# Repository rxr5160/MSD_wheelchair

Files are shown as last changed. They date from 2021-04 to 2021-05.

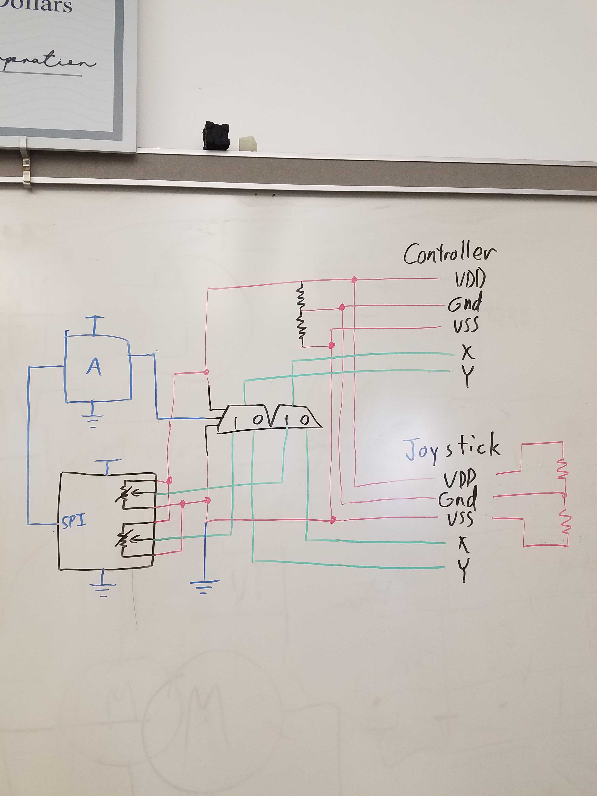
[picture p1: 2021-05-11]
Documentation/Media/Joystick/NewJoystickPCBdesign.jpg

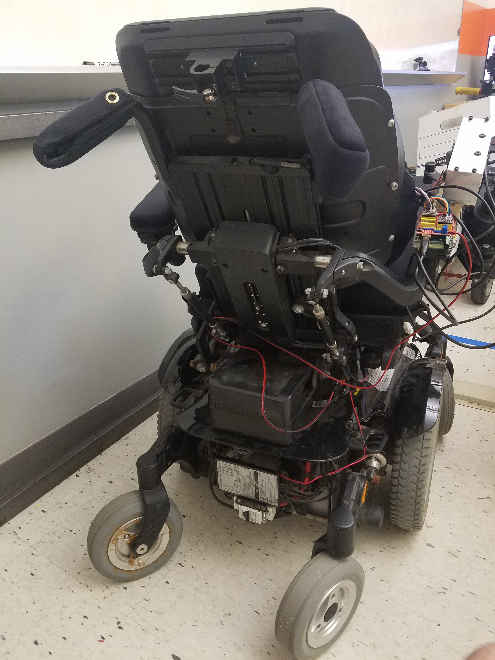
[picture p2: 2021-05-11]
Documentation/Media/Wheelchair/20200831_122622.jpg

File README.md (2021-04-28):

# MSD_wheelchair
MSD-21311 project, Mind-controlled Wheelchair

wheelchair -> main</br>
left_right -> object detection</br>
steering -> steering and acceleration control</br>
path_planning/ -> contains pathing files and map graph, runs Dijkstra shortest path</br>
	turn
	dijstra
	distance and direction maps
connection/ -> contains communcation code</br>
build.sh -> compiles system, bypass a makefile to run the command in shell</br>

<h3> code structure of Wheelchair main </h3>

- set global variables
	- next node idx
	- turning nodes -> prev, current, next IDs
	- total distnace traveled
	- distnace togo to next node
	- reset flag, boolean
- set start and end nodes from cmd arguments
- setup cameras
- get path through nodes
- set next node and distance to node 
- *loop*
	- get dstance traveled from camera
	- check if at the node -> z distance vs. togo distance
		- adjust total distance traveled
		- set next node and distance togo
		- set reset
	- if reset
		- reset camera pose
		- tell direction to turn
		- move turning node IDs forward
		- clear reset
	- check depth camera
		- adjust turn and acceleration signals as needed
	- send message to chair control of forward and turn intensity
- *end loop*

NOTES
=====
Tracking camera MUST have a USB3.0 controller or it throws an error

Several macros are used in debug for object detection
- ABS, prints average distance for each quadrent
- DET, prints quadrents with marks for threshold detection in each
- PDBG, prints signal it would want to send, turn left/turn right

Steering uses a quick and dirty PID of 10 elements to smooth steering, adjust size as needed (PID_SIZE in steering.cpp)

Object detection distance can be adjusted via the THRESH macro in wheelchair.h

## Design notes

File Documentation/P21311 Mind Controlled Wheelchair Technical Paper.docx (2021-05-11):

Project Number: 21311

# Mind Controlled Wheelchair

Cheyenne Dailey Computer Engineering | Sidney Davis Electrical Engineer

Ryan Radicello Computer Engineering | Dawson Hilk Electrical Engineer

# Abstract

This technical paper covers the integration of sensors onto an electric wheelchair to make it semi-autonomous, with minimal input from a device suited to a disabled individual. The team describes their use of the Intel RealSense 435 Depth Camera and T265 Tracking Camera, and how their initial plan to use a Raspberry Pi to perform Simultaneous Localization and Mapping (SLAM) evolved into using a laptop operating Linux to interpret basic sensor measurements. Furthermore, the process to use potentiometers to control the wheelchair’s joystick is described, along with the installation of two emergency stop buttons on the chair.

# Background

The Neurotechnology Exploration Team (NXT) Research Group at RIT is dedicated to using cybernetic techniques and physiological signals to create devices for those who rely on alternative methods. Adam Del Rosso is the project manager for an NXT initiative to create a wheelchair that responds to commands sent by a Brain Computer Interface (BCI). Upon realizing the need for more automation to relieve the effort required by the user, the wheelchair portion of the project was handed off as a Multidisciplinary Senior Design (MSD) project.

The MSD team intends to modify an electric wheelchair to accept limited commands from a BCI, as well as any input device best suited to the user’s disability. Furthermore, to compensate for the lack of command / user control, a method of machine vision has to be implemented, so the control over the heading of the wheelchair is a tandem effort between necessary decisions from the user and observing common sense decisions from the environment.

To stay within the scope of a 1-year project, NXT and the MSD team agreed that this device will only be tested indoors, on 1 floor of 1 building, and that limited setup instructions could be provided to the autonomous wheelchair software before beginning a run.

# Description of Design

The design of this project was broken down into two main sides, the software side, consisting of the camera control, communication, and mapping; and the hardware side, consisting of the joystick control and the emergency stop system.

The cost of the project was largely determined by the RealSense cameras. This cost was supplemented by the NXT budget as it costs a bit over three-hundred dollars for the pair. The MSD budget costs were also a little over three-hundred dollars for all other expenses. These included a wheelchair emulator to manually push and be able to test the system, a Raspberry Pi 4 and accessories, relays to handle the motor power in the emergency stop, cable extenders, printed circuit boards and components to control the joystick, and a bag to keep the laptop easily attached to the chair. The wheelchair itself was already owned and supplied by NXT.

## Software Design

When starting with the project, encouragement from our customer led to the decision to use Intel RealSense’s Depth Camera, D435, and Tracking Camera, T265, with their provided RealSense library. The team was under the assumption that these cameras were simple and easy to use with any operating system, ready for integration with full SLAM capabilities. This led most of the project with the goal to leverage SLAM and use it to make the wheelchair autonomous.

Under the above assumptions about the RealSense cameras and the availability of SLAM, the initial design was to connect with a Raspberry Pi 4 to have the processing power to handle both cameras and have the small form factor to integrate onto the wheelchair. Through much trial, error, and research, it was discovered that several assumptions were incorrect. Through testing and research, it was found that the T265 was no longer supported by RealSense and there was a critical error when interacting with a Pi that caused the communication with the camera to be cut off. After much deliberation it was decided that the best course of action was to transition to a laptop that was running a Linux OS, specifically Ubuntu 18.04, which was confirmed to connect to the T265 correctly.

With the processor adjustment, focus shifted to working with the cameras. The Intel RealSense D435 depth camera uses an infrared system to measure the distances. To satisfy the customer requirement of avoiding obstacles in the path of the chair in motion the pixels of the depth camera were divided into a grid of 16 segments. This allowed the system to know more accurately where an object was and what direction to turn the chair. Through this grid the steering control is determined via a proportional–integral–derivative controller (PID) and forward speed is based off of the steering amount. Both values are then sent to the Arduino to mechanically control the chair.

For navigation, the initial plan was to use the assumed SLAM capabilities stated to be provided by the Intel RealSense T265 Tracking Camera. This was set as a customer requirement from the very beginning. After thorough research and testing, it was found that given the time available and the experience/knowledge of the team that SLAM was unobtainable if a working product was to be delivered by the end of the term. Through much deliberation and discussion with the customer, it was decided to go with a node system on key locations or decision points with a weighted path system. From this node system, a start node and end node were given to a Dijkstra Algorithm to calculate the shortest path from start to finish and return it for execution. An adjacency list with weights is stored and read into the program on startup. This list allows Dijkstra's algorithm to find the best path to take and then direct the chair down said path to reach its destination. The system utilizes the T265 inertial measurement unit (IMU) to know how far the chair has moved and therefore whether it has reached a node and must change direction or not.

While cameras and mapping were essential, there was a need for communication protocols between the Arduino used for joystick control and the BCI client, designed by NXT, responsible for user input. The Arduino was designed to connect to a serial port on the laptop where messages were read and written to communicate. The server, created on the laptop, would write to the serial file, giving inputs for the X and Y magnitude from -100 to 100 that would be read by the Arduino and translated appropriately to control the joystick. The Arduino returned an acknowledgement message back to the main server stating whether the message was received successfully. The connection with the BCI was separate from the serial server, using ZeroMQ, an online concurrency framework that allows for socket connections. The zmq server was designed to create a socket with a PAIR configuration, allowing for uninterrupted communication between two sides. The server had one side of this, and the NXT team devised a client design that would connect via ethernet. This socket connection allowed for the transfer of JSON styled messages, with key/value pairs to be sent between each system. The BCI client would send a confirmation message that a connection was made with the server followed by a message stating the user’s chosen destination.

## Hardware Design

To control the motion of the wheelchair, the method used by a traditional user had to be fully understood. The joystick and accompanying electronics were removed from the arm of the provided wheelchair to learn what types of signals were sent from the joystick to the controller.

By using jumper wires to connect the joystick to a breadboard, and the breadboard to the controller, the voltages of each of the 8 pins were available to be probed. A labeled ground pin was found elsewhere on the controller to use as a reference, and then the voltage was recorded for the joystick in its rest position, forward position, reverse position, left position, and right position. As a result of this testing, the following table, and correlating functionalities was determined:

Table 1: Original Joystick Measurements and Functionality

Pin | Rest (V) | FWD (V) | RVS (V) | Left (V) | Right (V) | Function
1 | 2.5 | 2.5 | 2.5 | 2.5 | 2.5 | VDD
2 | 0 | 0 | 0 | -1 | 1 | X
3 | -2.5 | -2.5 | -2.5 | -2.5 | -2.5 | VSS
4 | 0 | 1 | -1 | 0 | 0 | Y
5 | 0 | 1 | -1 | 0 | 0 | Y
6 | 0 | 0 | 0 | 0 | 0 | Ground
7 | 0 | 0 | 0 | -1 | 1 | X
8 | 0 | 0 | 0 | 0 | 0 | N/C

The difference between ground and N/C was determined by probing the resistance compared to the reference point on the controller board. Ground reported as a short circuit, while N/C reported as an open circuit. Furthermore, the connectivity between the two X pins and two Y pins and determining whether they could be simplified to sharing the same pin, was tested experimentally using the first joystick emulator, described in a later portion of this document.

Steering the chair was important but so was stopping the chair in the case of an emergency, leading to the creation of the emergency stop design. The plan from the beginning was to cut off power to the motors only when either one of the buttons were pressed. Before we did this, we needed to figure out how to mount the buttons to the chair and come up with a schematic for how the components were to be connected. Luckily, there was a rail system on the sides of the chair that allowed for a button to be screwed to. The second button placement was talked about a little more. It was decided that the most convenient place for it to go was on the back right of the armrest. There was a 6m screw hole that we could use to fit the button with. This button had to fit an Arduino in it because it was the best place for it. It as 3d printed with these variables in mind. As for creating the schematic and how we planned to stop the chair. We decided on using a NO DPST (Normally Open Double Pole Single Throw) Relay in between the motor and the motor controller. For deciding to use the relay. It would allow us to use a smaller voltage and current to control the motor because without the relay, the buttons we had did not have a high enough amperage rating to match the motor. Buttons that could match that high rating were extremely expensive. Therefore, a 12V coil relay was chosen. We used a 24V to 12V converter from the battery, which is 24V, to get the relay coil voltage. The plan was to splice the power wire to the motor and hook that into the relay, but that would be a permanent fixture for the chair. Instead, an adapter of sorts was made instead that used quick disconnects to connect the wires that do not change into their original connections, and then also used quick disconnects to connect the motor to the relay and then the relay to the controller. This all fit nicely where the motors connected to the controller, and the relay was velcroed in a safe spot-on top of the controller.

# Supporting Feasibility Evidence

## Software Feasibility

To complete the mapping an adjacency list was created that correlated node numbers to locations and keep track of the distances between each that connected to another node. Dijkstra’s algorithm is used to find the best path from the start node to the end node by traversing the graph and tells the system how far to travel and to which node ID in the graph. The system then tells the Arduino to push the chair forward and the T265 IMU will determine when the target node has been reached. While this happens the D435 starts measuring in front of the chair with its infrared sensors to determine if there is something in the path, and if so, how to turn around the object and still make it to the target node. Each of these components were tested via walking through the mapped area with the cameras before doing the same with all connected. The map and pathfinding were validated by selecting locations and following the path given to be sure it matched what was expected and reached the correct location. The object detection was tested by doing a much shorter distance and watching a display of where the system saw objects in the grid created by the depth camera. The turn control was connected to the Arduino and LEDs were wired to display the turn and forward strength that the system was directing to the chair. All of these were then run simultaneously and walked through the mapped area to verify correct pathing, object detection, and steering control.

## Hardware Feasibility

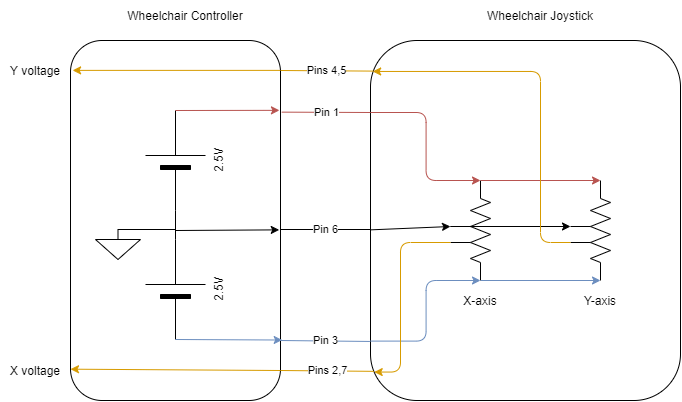
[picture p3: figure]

Figure 1: Observed Schematic of the existing Wheelchair Joystick/Controller Relationship

Based on the measurements in Table 1, the schematic above was derived. The joystick consists of two center-tapped potentiometers, and the wipers on the potentiometers are determined by the position of the joystick. A corresponding voltage is returned to the controller that is providing the positive and negative rails to both elements. Using this design, an equivalent circuit to the joystick was implemented on a breadboard using two 10k potentiometers and 2 equal resistors to make a voltage divider between the two rails to represent the center tap.

When connecting this breadboard to the wheelchair controller, the wheelchair screen showed no errors, and upon twisting the potentiometers the chair began to move, validating the schematic in Figure 1. The motors turned slower than anticipated, but this was later determined to be due to the position of the seat of the chair, which lowers the max velocity if the user is not reclined back past an internal threshold.

The overall E stop system had to be compact with very minimal wire exposure. This was to be something that you could hardly tell was there, except for the two buttons. The left rail button used four hex nuts that slid into the rails. The bottom of the button case was screwed into those nuts at the desirable position along the rail. The second button was 3d printed to fit the Arduino along with the top half of the button case which included the button part. The case had a whole in the bottom to be screwed to the armrest. It also had holes for the estop wires coming in and out, a hole for the wheelchair switch that controls whether the wheelchair is in manual or semi-autonomous mode, and holes for the Arduino wires. This all fit in a box that is about 4in x 4in x 4 in. The relay coil voltage required 12V, but the chair gave off 24V. To get this 12V, a 24V to 12V converter was needed. There was an open positive and negative terminal on the controller that the converter was hooked into to change the voltage to 12V. From this converter, the wires went to both E-stop buttons in series, as to shut off the power when a button was pressed, and then into the relay and back to the converter to complete the circuit. This was tested once these parts were implemented to see if the relay was switching on and off once a button or both buttons were pressed. The wheelchair previously had two black connecters from the motor that supplied power from the controller to the motor. These were disconnected and instead between the two, we used quick disconnects to connect the two again, but instead the power wires were diverted into the NO DPST relay and then back. This allowed the power to the motors to be cut as soon as an E-stop button was pressed. The wires and disconnects were able to fit under the plastic cover of the wheelchair and thus were hidden very well. The relay was velcroed securely to the top of the controller. The DC converter was able to be placed inside an existing component on the chair.

# Results, conclusion, and recommendations

This project initially had a budget of $1,000 total. Half of that came from RIT MSD funds, and the other half came from NXT’s budget. In total about $700 of it was spent. The RealSense camera bundle (tracking and depth camera) came from the NXT budget and all other purchases came from the MSD budget.

## Software Results

Mapping proved to be a success with the project. Tests with the emulator proved that the maps found the shortest path and that the nodes could be recognized based on distances. The one caveat to the design is the manual measurement of the distances using the T265 IMU. This created a potential point of failure as it was not always guaranteed that the chair would start in the same location. Keeping consistent for all our testing however, proved that the mapping solution to be accurate. The path planning for the system was handled by traversing the map using Dijkstra’s shortest path algorithm. This allowed for the system to know how to get from the starting point to the ending point with the least total distance covered, not just the least distance from the current node to the next map node. The adjacency list to create the map and tell the chair what direction to turn at each intersection based on the does before and after it were all successful. The chair was able to navigate following the mapped path and tell the user what direction to turn the chair. As the time on the project ran out, we would have liked to have been able to manipulate the gyroscope or pose data of the T265 to automatically turn the chair to face the correct direction.

For steering, thresholding was used with the location of an object in the depth frame along with the PID that was created. During testing and the demonstration, it was found that the design could drive the chair down the intended space avoiding most objects; however, it was not the cleanest driving. The PID designed was a quick method to get the baseline needed for correcting once a turn was made. This design did not receive the proper testing needed prior to demonstration that was required to have smooth steering. The result was over-correction and bouncing between walls. While this still achieved the drive goal of unassisted movement, an issue was run into in different hallways when doorways or corners were reached. This was either due to the PID design or to the thresholding done based on the depth camera. There was not sufficient time remaining to flush out and resolve the problem.

Testing was completed to confirm that each connection, serial and socket, could be made with messages successfully passed between the devices. The first test was with the serial connection for the Arduino. Messages containing x direction and y direction magnitudes were sent from the main program to the Arduino and translated into the proper joystick voltages. Testing proved successful by a handoff test where the program sent inputs to the Arduino without user assistance. One caveat found with the Arduino was that when it was first connected, there would be a hard fault that would prevent the program from running. After terminating the program and restarting it, this was no longer an issue.

The BCI socket connection was tested next, using a simple python client program that would connect to the ZeroMQ server, and pass the two messages. Testing was done to ensure that the correct messages were received, and that the information could be parsed from the JSON message format. One issue that occurred with the socket design was creating a non-blocking receive that could allow for the user to issue stop and start commands whenever they pleased. Given the remaining time and the debugging necessary to resolve this issue, it was accepted that allowing for these messages would not be achievable.

## Hardware Results

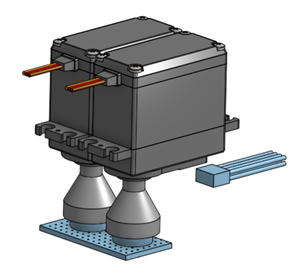
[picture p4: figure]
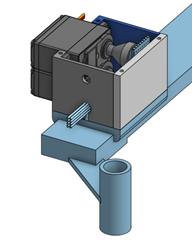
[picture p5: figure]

Figure 2: Design out of Case | Figure 3: Design in Case on Wheelchair Arm

As a last resort, when V2 was producing the correct voltages but the chair refused to accept it as input, I fell back on the physical potentiometers I used to verify the joystick implementation in section 2.3. Connecting these potentiometers to a protoboard with resistors acting as the center-taps mimics the same circuitry as before, so attaching servos to the heads of the potentiometers provides electrical control from the Arduino, making the system go from electrical, to mechanical, back to electrical. The servos, potentiometers, and protoboard are given a case that can screw into the right arm of the wheelchair, midway between the pre-existing Arduino case and the wheelchair joystick.

The servos do not always return exactly to the center position, depending on whether it is rotating clockwise towards the center vs rotating counterclockwise towards the center. This causes an error on boot for the wheelchair if not perfectly centered, but a quick fix is to set the potentiometers off center in the Arduino Code on boot, return to center, and then try powering on the wheelchair. If this does not work, set the potentiometers to rotate in the opposite directions on boot, then return to center.

For more information about the Joystick Controller PCB, please refer to “P21311 Joystick Controller Documentation.docx”

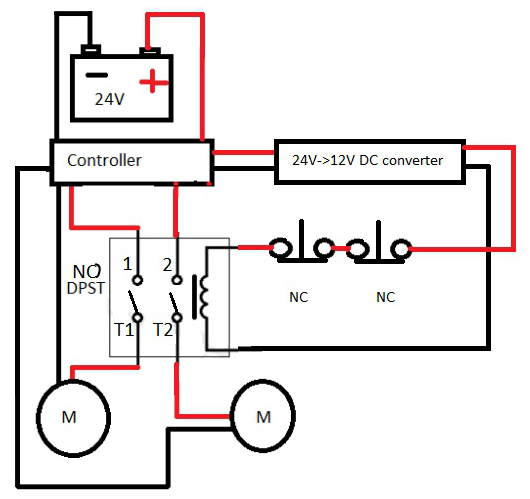
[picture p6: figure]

Figure 4: Emergency Stop Schematic

There were some things on the estop system that did not initially work as planned. The converter that was on the chair from the last team, did not work at all. This was replaced with a new DC-DC converter. The original design of the system included a NC DPST relay so that the motors would always be connected unless the E-stop buttons were hit in which case the relay would get power and flip open the Motor connections. After careful deliberations with the team, for safety purposes and practice, it was changed to be a NO DPST relay. It will now only run when power is supplied to the relay and so when a button is hit, the relay coil will lose voltage and flip open the motor connections. This electrical schematic for the final design and prototype is shown in Fig. 4. Once all the components were in place, which are the two buttons, the DC converter, and the relay adapter, the chair E-stop system was tested repeatedly. We tested for how abrupt the stop would be at different stops and how far the chair rolled after a button was pressed. These values were under what our Engineering requirements were. It was therefore labeled as a success. There were some small things the team would do differently when creating this system. The first is always having someone double checking the cad prints. Some prints were not done exactly right the first time due to some stupid mistakes. This could have saved a lot of time if done right the first time. The only other thing that would be done differently are the quick disconnects connecting the motors, relay, and battery. Some of these disconnects were “Macgyvered'' to fit the overly sized pins on the chair’s motor connection port. The quick disconnects fit well currently, but they are probably the only type of their kind in their current state. We would have liked to do a little more digging on the internet to find the right sized quick disconnects. The future work of this subsystem can vary wildly or not at all. This entire system is designed so that it can be replaced or removed if someone deems it necessary. Nothing was done so that it was permanently attached to the chair.

# Acknowledgments

Thank you, to our customer, Adam Del Rosso from the Neurotechnological Exploration Team at RIT. NXT provided an electric wheelchair, and sponsored purchasing components critical to the completion of the objective. Adam also dedicated an impressive weekly commitment to meeting with the team and offering his technical expertise and experience towards our common goals.

Thank you, to our guide, Charles Hacker from L3 Harris. He assisted the team with interpreting project management requirements and understanding the generic systems in place to help us with our current project, as well as how to apply the same systems towards our future projects. He also proved valiant at the generation and research of alternative ideas whenever we discovered our methods were not going to work.

Thank you to the Multi-Disciplinary Robotics Club (MDRC) at RIT, for allowing us to use your club room and tools as a workspace. Having a private space with dedicated tools and equipment allowed for a great boost in efficiency while prototyping.

Thank you to Multidisciplinary Senior Design, for supplementing our funding and providing us with the resources, modules, and feedback to organize and complete our project.

Thank you to Carlos Barrios, for your advice on integrated circuit selection.

Kate Gleason College of Engineering Rochester Institute of Technology Rochester, New York 14623

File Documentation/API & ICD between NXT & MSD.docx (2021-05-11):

# Application Programming Interface

# & Interface Control Document

Collaboration between: MSD P21311 and NXT

The two systems to communicate between shall be referred to as “The Headset” and “The Wheelchair”. This is incorrect from a literal standpoint, but the hardware to be used is still undecided.

Wheelchair opens connection, waiting for peripheral devices such as the headset

ICD Characteristics to use based on Application Intentions

Physical Medium to communicate over:

- Ethernet

Data Structure:

- Command with arguments
- 1 Command per action

Potential Programming Languages and Pertinent Libraries

C and/or python

Allow for Multi-language support

zero-MQ vs active-MQ

Application Level Protocol: all data to be passed using JSON key-value pairs

- Both systems will have an agreed upon list of known locations to select from. When the user chooses one of these locations, the headset will send that location (a unique, alphanumeric string) to the wheelchair.
- Wheelchair operates in a series of states:
  a. IDLE until device connected
  b. Remain STOPPED until location received
  c. Begin MOVING when destination received
    - While moving, if stop command received, halt motors, wheelchair ack to headset once stopped.
      - A new destination could be selected in this state. Expect either a start command or the name of the new destination.
    - Add left / right vector commands for the sake of troubleshooting
  d. FINISHED if the destination is reached, ack sent to headset once achieved.

Questions from Cheyenne:

1. What are you looking for/expecting from the ack messages from the chair to the headset?
2. Do you know the full format of the message being sent? Or is it simply done with ZeroMQ (assuming headset side is using python?) with something along the lines of:

socket = context.socket(zmq.REQ)

socket.connect("tcp://127.0.0.1:5000")

socket.send_json(data)

3. You wanted to use a PAIR socket connection correct?
4. How do you want the locations list?

| 0 Aero Lab
| 1 Engineering Hall
| 2 Thermal Analysis Lab
| 3 Student Services
| 4 MechE Corner
| 5 MechE Office
| 6 2149
| 7 Thermal Hall Connection
| 8 Dr Du's office
| 9 Gordon Atrium
| 10 Xerox
| 11 Women In Engineering
| 12 Atrium Center

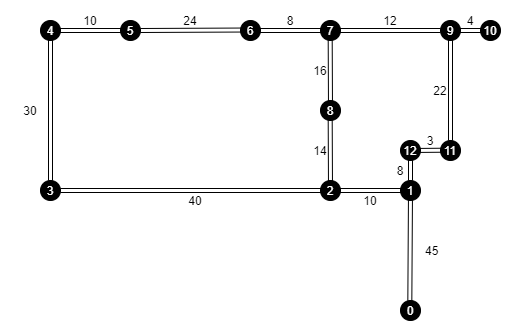
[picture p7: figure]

RIT Second Floor Gleason Blueprints: J:\Design & Construction\Web Dwgs\Bldgs strippt\009-stripped\009-2stripped Layout1 (1) (rit.edu) (https://www.rit.edu/fa/facilities/system/files/floorplans/1/009-2.pdf)

~~{~~

~~“Wheelchair update”: {~~

~~“State”: “STOPPED/MOVING”,~~

~~“Reason”: “Destination reached/user initiated”~~

~~}~~

~~}~~

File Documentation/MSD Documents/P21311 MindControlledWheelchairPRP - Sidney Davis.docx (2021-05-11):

Multidisciplinary Senior Design

Project Readiness Package

Prepared by Sidney Davis, April 20, 2020

Project Title | Mind-Controlled Wheelchair
Project Number | P2XXXX
Primary Customer | Neurotechnology Exploration Team
Sponsor | MSD & Neurotechnology Exploration Team
Faculty Champion | [Optional, assigned by MSD]
Other Support | Multi-Disciplinary Robotics Club
Project Guide | [Assigned by MSD]
IP Considerations (must pick one) | a) IP assigned to [organization]

When complete, please submit this document through our online form, located at https://goo.gl/forms/J3G8G2jhTUFuJCYe2

Project Information

Overview

Make modifications to a mechanical wheelchair such that it can semi-autonomously drive in a populated environment with occasional heading information, ideally provided by an OpenBCI headset, but modifiable enough to receive commands from other devices if desired.

Preliminary Customer Requirements (CR)

- Use of three-dimensional imaging to observe and interpret the environment
- Identify locations that require a “Decision” to be made by the user, like an intersection
- Continuous path planning to avoid dynamic obstacles (i.e. pedestrians)
- Establish a communication protocol to receive occasional heading information from any compatible input device
- Weekly Customer-Team communication

Preliminary Engineering Requirements (ER)

- Simultaneous Localization and Mapping (SLAM)
- Ability to identify dynamic and stationary obstacles from the front of the wheelchair
- Interpret heading instructions from an external device through serial communication such as
  - FORWARD
  - ROTATE LEFT
  - ROTATE RIGHT
  - STOP
- Frequency of instructions received should correlate to the user’s control
  - More commands within period: user is describing how to move now
  - Less commands within period: drive autonomously unless at a decision point

Constraints

- Use of the wheelchair supplied
- The use of at least two Intel RealSense Cameras

Project Deliverables

Minimum requirements:

- All design documents (e.g., concepts, analysis, detailed drawings/schematics, BOM, test results)
- Working prototype
- Technical paper
- Poster
- All teams finishing during the spring term are expected to participate in ImagineRIT

Additional required deliverables, if needed:

- Demonstrations of overall hardware to sponsors and possibly media as opportunities arise.

Budget Information

- Wheelchair: already provided by sponsor
- 2x Intel RealSense Depth Cameras: $355.98
- 1x Intel RealSense Tracking Camera: $199.00
- Central Processing Unit: TBD
- Supporting hardware: ~$50

Intellectual Property

None

U.S. Citizenship

None

Travel Opportunities

None foreseen

Project Resources

Anticipated Student Staffing by Discipline

Department | Expected Activities
Biomedical Engineering | None
Computer Engineering | Cheyenne Dailey, +1: Create program to interpret measurements taken by the Intel RealSense Camaras; generate “ideal path” from camera data.
Electrical Engineering | Sidney Davis, +1: System connections and power distribution; develop communication protocol from user controller; control motors to follow path as reported by cameras
Industrial & Systems Engineering | None
Mechanical Engineering | None
Other | Members of the Multidisciplinary Robotics Club will fill the “+1” gaps in the afore mentioned fields

Required Resources

Describe the resources necessary for successful project completion. When the resource is secured, have the responsible person initial and date to acknowledge that they are aware and agree. We assume that all teams with ME/ISE students will have access to the ME Machine Shop and all teams with EE students will have access to the EE Senior Design Lab, so it is not necessary to list these. Limit this list to specialized expertise, space, equipment, and materials.

Faculty
Environment
Equipment
Materials
Other

RIT Kate Gleason College of Engineering Project Readiness Package Multidisciplinary Senior Design Template Revised Fall 2018

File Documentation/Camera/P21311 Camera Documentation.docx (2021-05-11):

File: P21311 Camera Documentation

MSD Team: Mind Controlled Wheelchair

Owner: Cheyenne Dailey - cjd9104

Date: 2/8/2021

Purpose 2

Overview 2

Design Choice 2

Resources 3

Installation 3

Ubuntu Image 3

Librealsense and RealSense Viewer 3

Code Samples 4

D435 Depth Camera 5

Specs 5

Intel RealSense Viewer 6

Observations 7

T265 Tracking Camera 7

Specs 7

Intel RealSense Viewer 8

Observations 9

# 1. Purpose

## 1.1. Overview

In order to operate in a semi-autonomous state, a method of viewing the surrounding environment along with mapping the environment was necessary for safe movement and navigation. To accomplish this, a camera system that could detect objects and map a location was desired. A recommended method of implementing this was to use Simultaneous Localization and Mapping Algorithms (SLAM) Mapping.

## 1.2. Design Choice

Our customer recommended looking into Intel RealSense Depth and Tracking Camera Bundle (https://store.intelrealsense.com/buy-intel-realsense-depth-and-tracking-bundle.html). This bundle included the D435 Depth Camera with the ability to detect an object’s distance away from the camera. It also included the T265 Tracking Camera which has built in V-SLAM technology that would run directly on the device. Upon further research, an open source library was found, librealsense, that integrates with Intel RealSense devices, allowing for easier integration as well as an application for viewing camera output and example code for basic camera tasks (distance reading, pose reading, multi camera interfacing, recording, etc.). Another feature available with using the Intel RealSense SDK is the provided wrappers. By default, most of the SDK code was written in C++, along with the examples. The wrapper option allows for the choice of which language to write in; ROS, Python, Matlab, OpenCV, etc. These factors led us to believe that using these cameras was the best course of action.

The second decision that had to be made was what type of processing system would be used. Initially a Raspberry Pi 4 was selected due to its low power consumption, size, and cost. After much testing it appeared that there was always an error or some aspect of the camera functionality that was non-operable. With much research it was discovered that the 265 Tracking Camera was known for these bug issues and Intel had discontinued support for the device. After scouring different support forums, it was found that the Raspberry Pi was the likely cause of the issue, and that using a laptop would be a better option to use the cameras.

The options with a laptop were to use a Windows OS or a Linux OS. After much consideration, it was decided that using a Linux OS would be the best course of action. Linux allowed for easier compilation of code and examples. Using a team members laptop initially, a Linux OS, Ubuntu 18.04.5, was set up and used. Upon testing, all the previous issues faced with the Raspberry Pi 4 were gone, allowing for seamless multi-camera integration.

# 2. Resources

1. ~~Raspberry Pi 4~~
  a. ~~Power Cable~~
  b. ~~Micro HDMI to HDMI~~
2. ~~Monitor~~
3. ~~Mouse/Keyboard~~
4. Laptop with Linux OS - Ubuntu 18.04
5. Intel Realsense Depth Camera D435
6. Intel Realsense Tracking Camera T265

# 3. Installation

## 3.1. Ubuntu Image

The laptop used was booted with a Linux OS (ubuntu-18.04.5-desktop-amd64.iso).

## 3.2. Librealsense and RealSense Viewer

The first course of action is to clone the github repository for the Intel Realsense Library, librealsense, using the following command.

>> git clone https://github.com/IntelRealSense/librealsense.git

>> cd librealsense/

The instructions that were followed for installing the Librealsense library and RealSense Viewer can be found here (https://dev.intelrealsense.com/docs/compiling-librealsense-for-linux-ubuntu-guide). For simplicity, follow the instructions below.

Setup Preliminaries

>> sudo apt-get update && sudo apt-get upgrade && sudo apt-get dist-upgrade

>> sudo apt-get install git libssl-dev libusb-1.0-0-dev pkg-config libgtk-3-dev

>> sudo apt-get install libglfw3-dev libgl1-mesa-dev libglu1-mesa-de

>> sudo cp config/99-realsense-libusb.rules /etc/udev/rules.d/

>> sudo udevadm control --reload-rules && udevadm trigger

Patch to the kernel

>> ./scripts/patch-realsense-ubuntu-lts.sh

Build Librealsense

>> sudo add-apt-repository ppa:ubuntu-toolchain-r/test

>> sudo apt-get update

>> sudo apt-get install gcc-5 g++-5

>> sudo update-alternatives --install /usr/bin/gcc gcc /usr/bin/gcc-5 60 --slave /usr/bin/g++ g++ /usr/bin/g++-5

>> sudo update-alternatives --set gcc "/usr/bin/gcc-5"

>> mkdir build && cd build

>> cmake ../

>> sudo make uninstall && make clean && make && sudo make install

# 4. Code Samples

Online code samples can be found for different camera functionality, for both individual use and multi camera use. Intel RealSense provides sample code within the librealsense library here (https://github.com/IntelRealSense/librealsense/tree/master/examples) and descriptions of what those examples do along with which camera(s) are used can be found here (https://dev.intelrealsense.com/docs/code-samples).

# 5. D435 Depth Camera

## 5.1. Specs

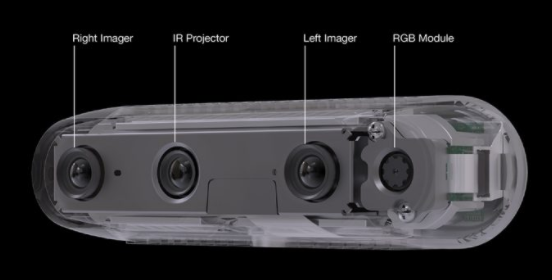
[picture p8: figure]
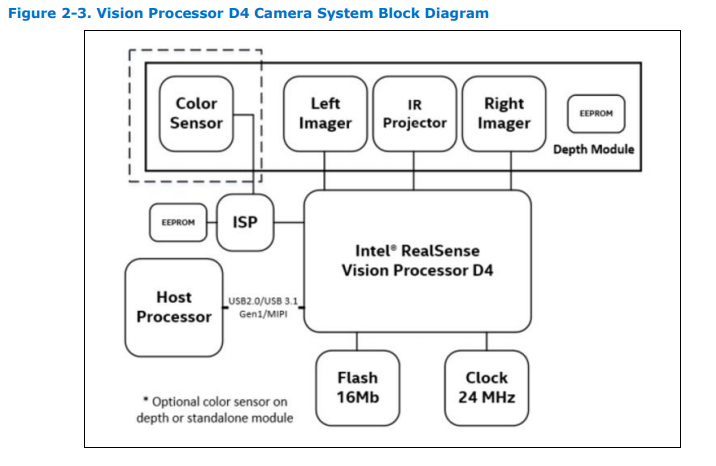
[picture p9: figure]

Depth Technology | Active IR Stereo
Main Intel RealSense Component | - Intel RealSense Vision Processor D4 - Intel RealSense Module D430 + RGB Camera
Depth FOV | 85.2𝆩 x 58𝆩 x 94𝆩 (+/- 3𝆩)
Depth Stream Output Resolution | Up to 1280 x 720
Depth Stream Output Frame Rate | Up to 90 fps
Minimum Depth Distance (Min-z) | 0.1m
Maximum Range | ~10 Meters (varies depending on settings)
RGB Sensor Resolution and Frame Rate | 1920 x 1080 at 30 Frames per second
RGB Sensor FOV | 69.4𝆩 x 42.5𝆩 x 77𝆩 (+/- 3𝆩)
Dimensions | 90 mm x 25 mm x 25 mm
USB | USB-C* 3.1 Gen 1
Mounting | - One 1/4-20 UNC thread mounting point - Two M3 thread mounting points

## 5.2. Intel RealSense Viewer

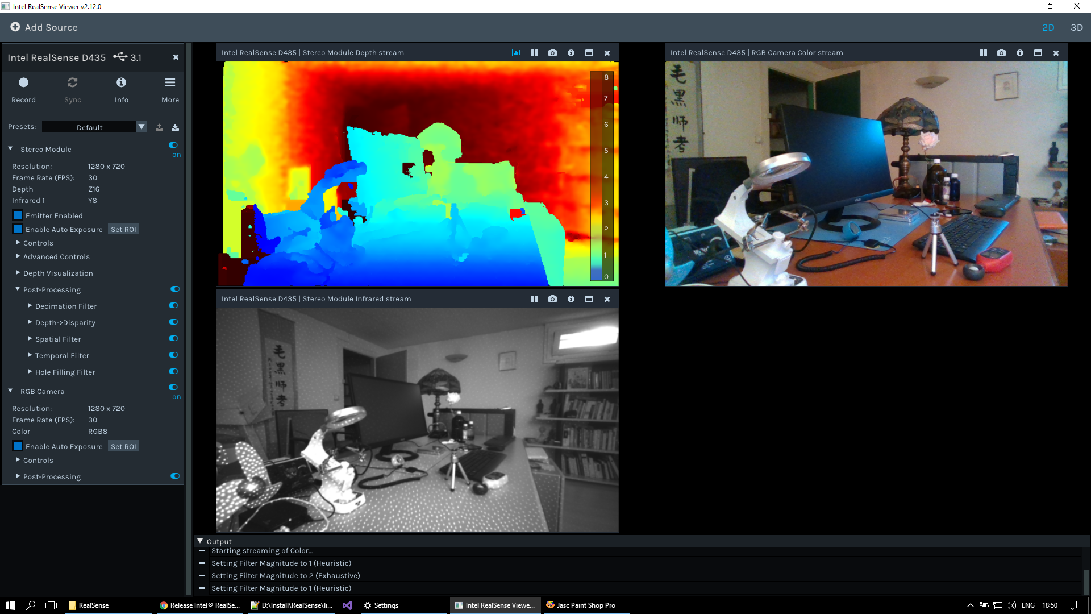
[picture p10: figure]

There are three viewing options with the Intel RealSense Viewer 2D rendering for the depth camera. The upper left hand corner the Stereo Module Depth Stream, using color coding to distinguish the distance each object is being registered at. Shades of blue represent closer objects while shades of red denotes objects further away. The upper right image shows the RGB Color Camera Stream. This is a realtime colored image of what is seen by the depth camera. The last view, the bottom left corner, is the Stereo Module Infrared Stream. This stream utilizes dots to provide a rendering of how dense the object it is viewing appears. The closer and more solid the object, the more dots used to distinguish the object’s location.

## 5.3. Observations

1. Accurate depth readings tend to be within the range of 0.2m and 2m generally

# 6. T265 Tracking Camera

## 6.1. Specs

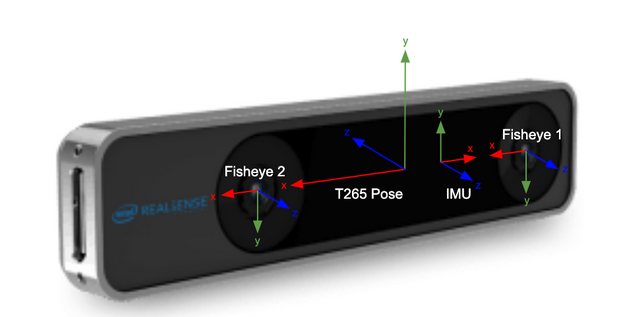
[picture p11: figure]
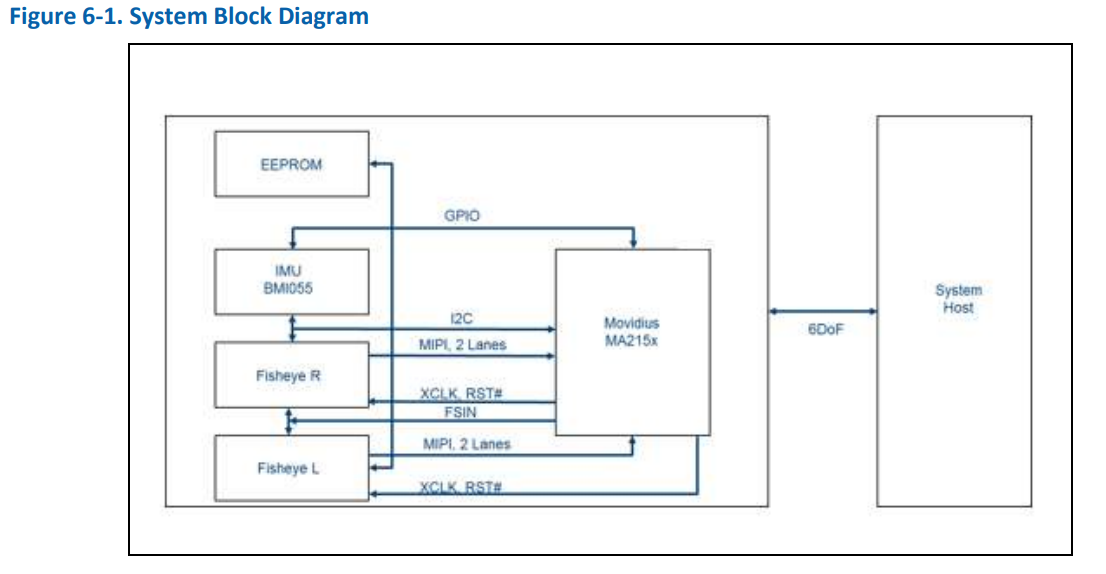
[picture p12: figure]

SLAM | V-SLAM : High Precision Visual Inertial Odometry Simultaneous Localization and Mapping algorithms
VPU | Intel Movidius Myriad 2.0 VPU : Visual Processing Unit optimized to run V-SLAM at low power
FOV | Two Fisheye Lenses with combined 163+5° FOV: Two OV9282 imagers with fisheye lenses for a combined, close to hemispherical 163±5° field of view for robust tracking even with fast motion.
Inertial Measurement Unit (IMU) | BM1055 IMU : allows for accurate measurement of rotation and acceleration of the device, to feed into the V-SLAM algorithms
USB | USB 3.1 Gen 1 Micro B : USB 2.0 and USB 3.1 supported for either pure pose data or a combination of pose and images
Dimensions | 108 mm x 24.5 mm x 12.5 mm
Mounting | 2 x M3 0.5 mm pitch mounting sockets

## 6.2. Intel RealSense Viewer

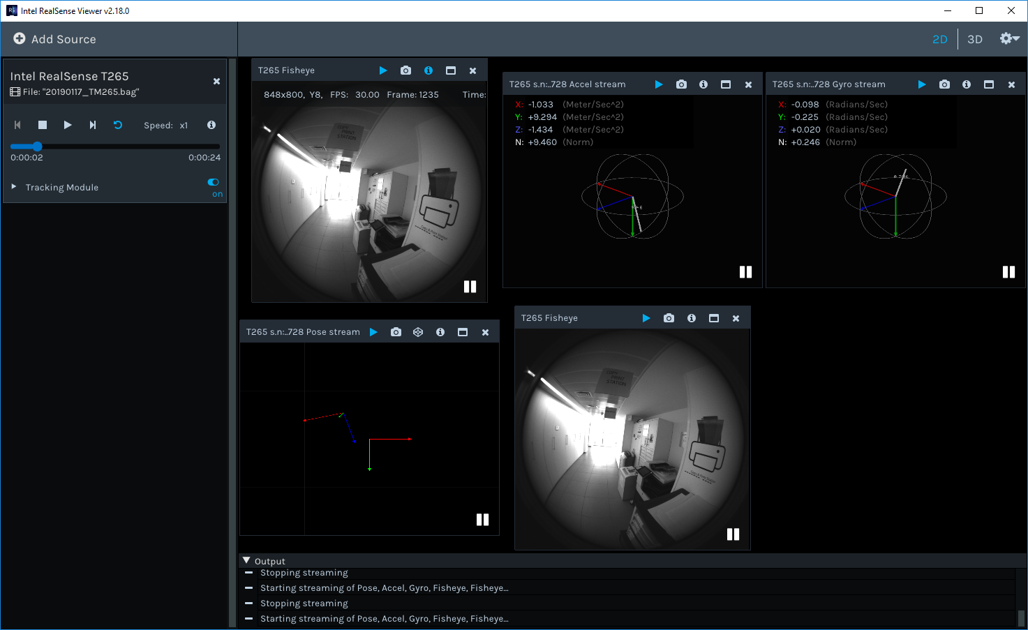
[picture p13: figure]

There are five different viewing windows for the Tracking Camera. Two, the top left and the bottom middle, represent the view from the fish-eye lens equipped with the camera. The top middle is the Accel Stream which displays the direction of acceleration that the tracking camera is moving in. The top right is the Gyro Stream which displays the tilt of the camera from its starting position. Lastly, the bottom left is the Pose Stream. This stream tracks the directions of change from the starting position of the tracking camera.

## 6.3. Observations

NOTE: If the tracking camera is not registering with the example code, open the realsense-viewer. Make sure that the tracking camera is connected. Select “MORE” then select “Hardware Reset”. After that please try to run the example again

# 7. Object Detection Design

The design implemented for our object detection relies solely on the depth camera, D435. The D435 supplies a frame of pixels, the height 480 pixels and the width 848 pixels, each corresponding to a specific distance. To determine an accurate measurement of the distance of an object, an average of a group of pixels is taken. The provided depth sample code from Intel RealSense takes an average of the entire frame, returning the overall, average depth distance that is being viewed by the camera.

For the purpose of this project, the single average was insufficient to accurately report where and how far away objects were. To remedy this, the frame was first split into three columns, providing left, middle and right.

Left | Middle | Right

This was tested with different objects in different locations and the results proved to be lacking in the accuracy that we were striving to achieve. There were instances where the floor being registered skewed the whole column’s values which was not ideal. To remedy this, it was decided to try splitting the frame into a 4x4 grid, with 16 unique quadrants. This would allow for more specific recognition of where objects were and if they needed to be avoided. The resulting grid is as follows:

Q0 | Q1 | Q2 | Q3
Q4 | Q5 | Q6 | Q7
Q8 | Q9 | Q10 | Q11
Q12 | Q13 | Q14 | Q15

This larger breakdown of the frame allowed for a better idea of where the object detected was in relation to the chair. The lower quadrants, Q12 - Q15 were ignored in testing with the emulator as it was registering the floor. This was modified of the occasion when the camera was angled high enough to avoid registering the floor the entire time.

The quadrants allowed for the identification if an object was in the direct path of the chair or if it was simply registered by the camera. The division also allowed for the recognition of if the chair needed to move to the left or the right to avoid a detected object, and how hard/far

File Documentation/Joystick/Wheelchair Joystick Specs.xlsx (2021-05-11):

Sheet: Voltages
voltages probed between live wires and ground pad on PCB. fwd, rvs, left and right refer to pushing the joystick to it's max position and measuring the resulting voltage
from perspective of PCB
2 | 4 | 6 | 8
1 | 3 | 5 | 7
pin | rest (V) | fwd (V) | rvs (V) | left (V) | right (V) | Observed Func
1 | 2.5 | 2.5 | 2.5 | 2.5 | 2.5 | Vdd
2 | 0 | 0 | 0 | -1 | 1 | X val 1
3 | -2.5 | -2.5 | -2.5 | -2.5 | -2.5 | Vss
4 | 0 | 1 | -1 | 0 | 0 | Y val 1
5 | 0 | 1 | -1 | 0 | 0 | Y val 2
6 | 0 | 0 | 0 | 0 | 0 | Gnd X
7 | 0 | 0 | 0 | -1 | 1 | X val 2
8 | 0 | 0 | 0 | 0 | 0 | NC
current | vcc | vdd
any config | 19.2mA | 19.2mA
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

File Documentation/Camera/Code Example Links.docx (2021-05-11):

Examples look to be all C++ Utilize realsense libraries in the intel skd from the dev page:

https://www.intelrealsense.com/developers/

Python wrapper Documentation

https://intelrealsense.github.io/librealsense/python_docs/_generated/pyrealsense2.html#module-pyrealsense2

Code examples:

https://dev.intelrealsense.com/docs/code-samples?_ga=2.108028034.1289909343.1599752137-1488677268.1598372452

https://github.com/IntelRealSense/librealsense

https://www.intelrealsense.com/autonomous-navigation-using-intel-realsense/

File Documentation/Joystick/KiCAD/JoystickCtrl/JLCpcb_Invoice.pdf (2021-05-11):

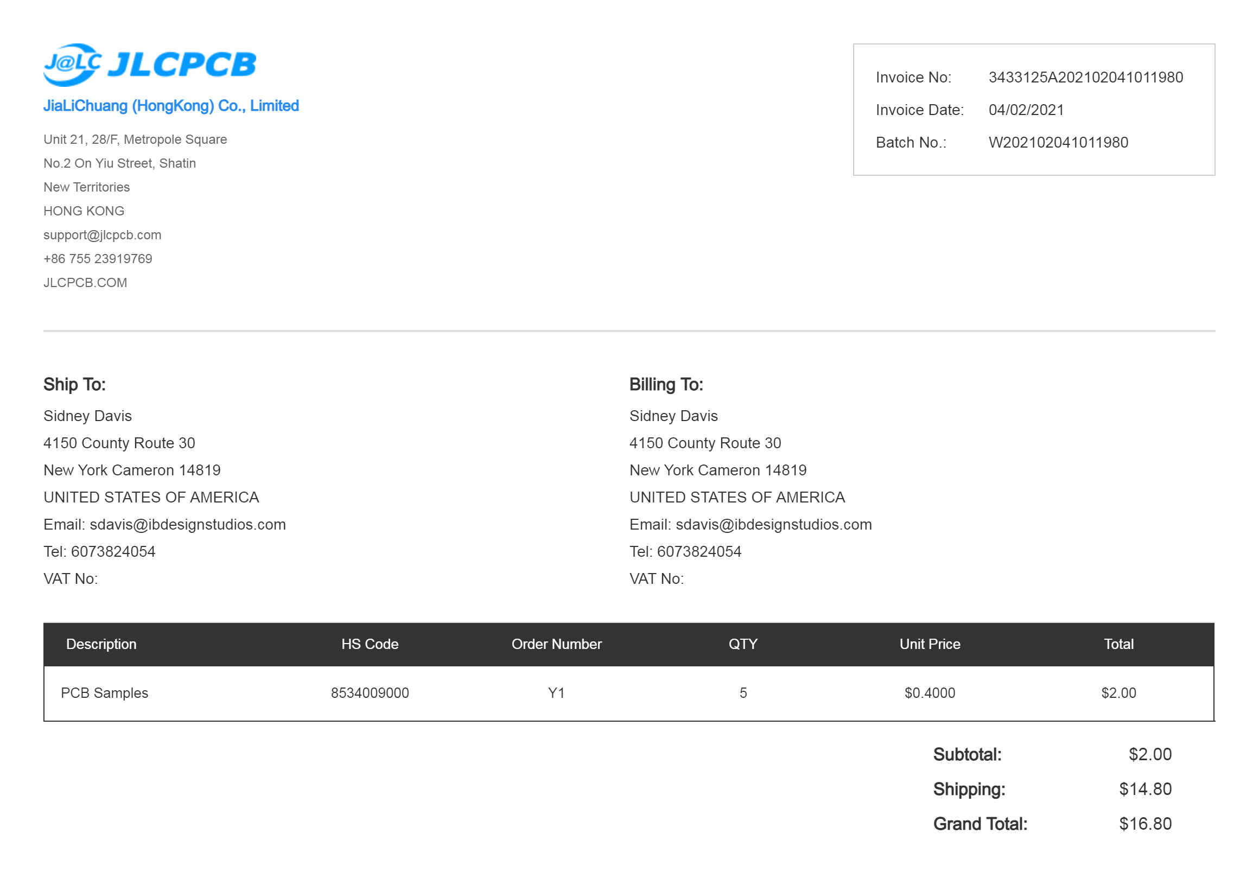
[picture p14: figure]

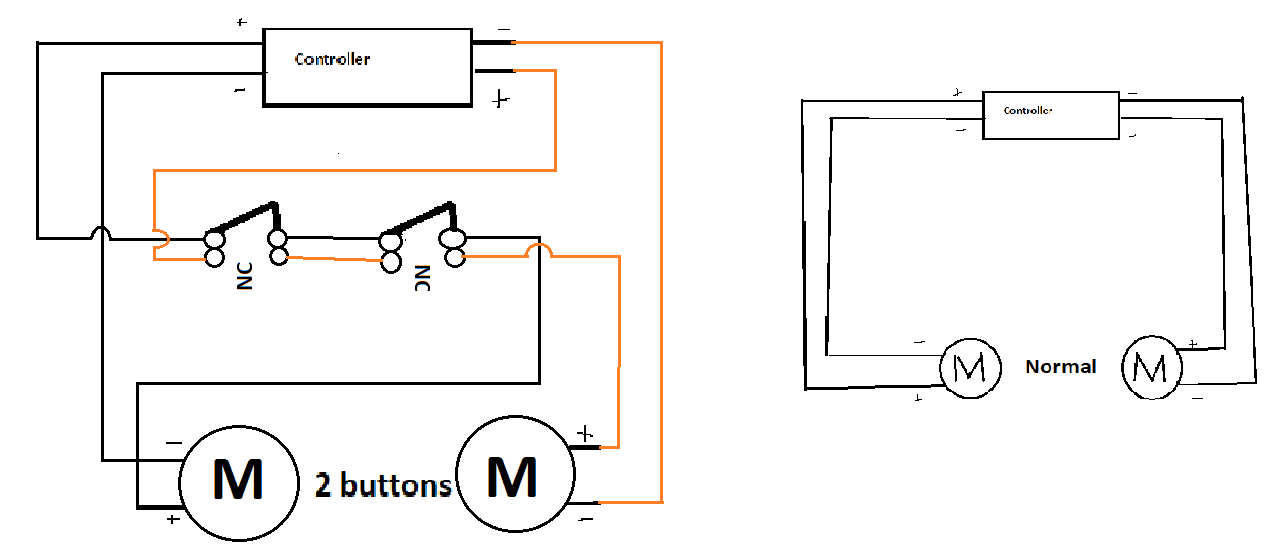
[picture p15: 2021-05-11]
Documentation/Media/Wheelchair Accessories/Button schematic.png

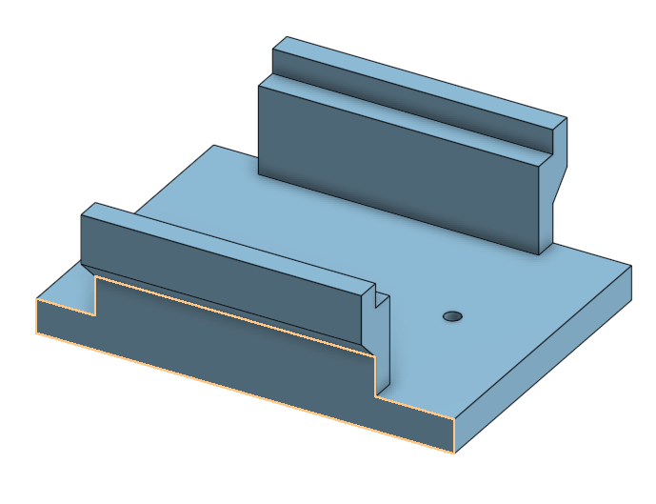
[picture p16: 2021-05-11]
Documentation/Media/Wheelchair Accessories/RasPI mount.1.PNG

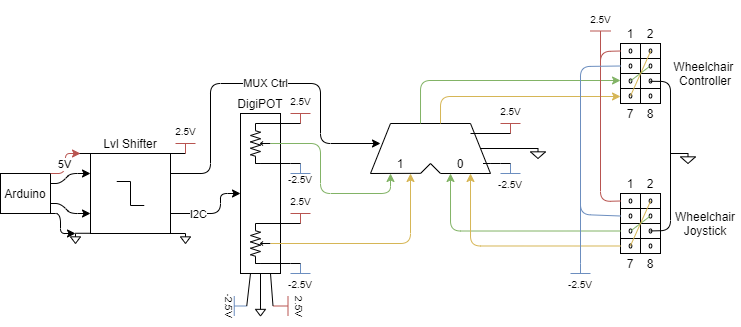
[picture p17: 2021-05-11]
Documentation/Media/Joystick/JoystickCtrlV2.png

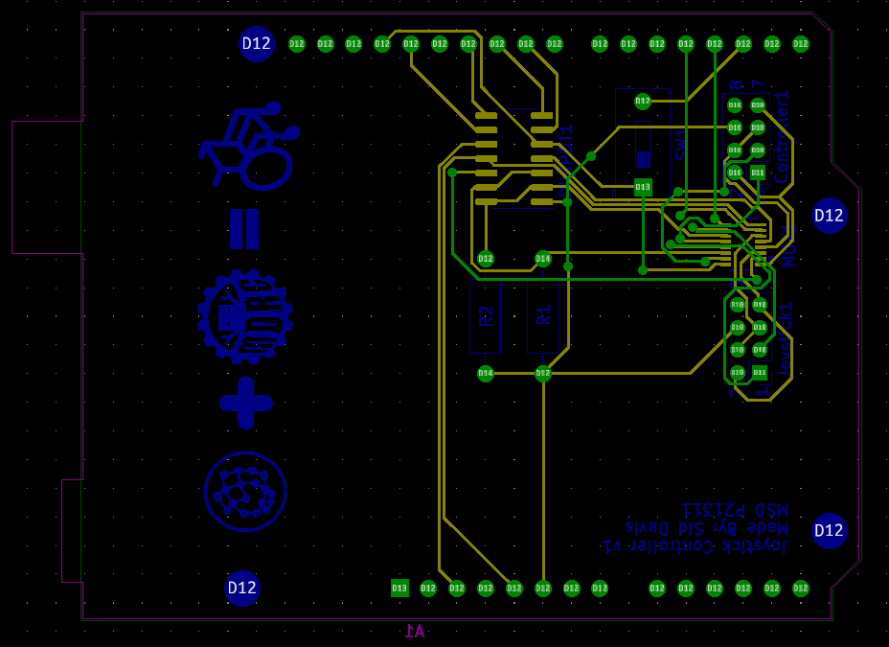
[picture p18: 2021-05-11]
Documentation/Media/Joystick/PCB-Gerber.PNG

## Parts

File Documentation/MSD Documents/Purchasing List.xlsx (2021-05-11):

subsystem | Purchaser | Item | URL | Unit Price | Quantity | MSD Account | NXT Account | shipping | comments |  | total cost | MSD Funds | NXT Funds | MSD Budget | NXT Budget
Cameras | Adam | Intel Camera Bundle | https://store.intelrealsense.com/buy-intel-realsense-depth-and-tracking-bundle.html | $378.13 | 1 | FALSE | TRUE |  | shipping included |  | $378.13 | $500.00 | $121.87 | $500.00 | $500.00
 |  |  |  |  |  |  |  |  |  |  |  | $500.00 | $121.87
 | Ryan | Raspberry Pi 4 kit |  | $107.95 | 1 | TRUE | FALSE |  |  |  | $107.95 | $392.05 | $121.87
Emulator | Sid | PVC Pipe | https://www.lowes.com/pd/Charlotte-Pipe-1-in-dia-x-2-ft-L-450-PSI-PVC-Pipe/3341536 | $2.50 | 2 | TRUE | FALSE | $0.00 | pickup |  | $5.00 | $387.05 | $121.87
Emulator | Sid | PVC Joint | https://www.lowes.com/pd/LASCO-1-in-x-1-in-x-1-in-x-1-in-dia-Tee-PVC-Fitting/1067669 | $1.34 | 2 | TRUE | FALSE |  |  |  | $2.68 | $384.37 | $121.87
Emulator | Sid | Elbow Bracket | https://www.lowes.com/pd/National-Hardware-2-1-2-in-Steel-Zinc-Plated-Corner-Brace/1000390945 | $3.98 | 4 | TRUE | FALSE |  |  |  | $15.92 | $368.45 | $121.87
Emulator | Sid | Dolly Cart | https://www.lowes.com/pd/Milwaukee-1000-lb-4-Wheel-Wood-Dolly/4765247 | $21.98 | 1 | TRUE | FALSE |  |  |  | $21.98 | $346.47 | $121.87
Emulator | Sid | Portable Monitor | https://www.amazon.com/gp/product/B07W51P9NG/ref=ppx_yo_dt_b_asin_title_o00_s00?ie=UTF8&psc=1 | $84.00 | 1 | FALSE | FALSE |  | already aquired |  | $84.00 | $346.47 | $121.87
Emulator | Sid | Battery Bank | https://www.amazon.com/gp/product/B083VYW2TM/ref=ppx_yo_dt_b_asin_title_o00_s00?ie=UTF8&psc=1 | $29.99 | 1 | FALSE | FALSE |  | 2 pack, already aquired |  | $29.99 | $346.47 | $121.87
 |  |  |  |  |  | FALSE | FALSE |  |  |  | $0.00 | $346.47 | $121.87
 |  |  |  |  |  | FALSE | FALSE |  |  |  |  | $346.47 | $121.87
 |  |  |  |  |  | FALSE | FALSE |  |  |  |  | $346.47 | $121.87
Mounts | Dawson | PGYTECH Action Camera Universal Mount | https://www.bhphotovideo.com/c/product/1468062-REG/pgytech_p_18c_032_action_camera_universal_mount.html/specs | $9.90 | 1 | TRUE | FALSE | $10.00 |  |  | $19.90 | $326.57 | $121.87
Joystick | Sid | DC-DC Converter | https://www.digikey.com/en/products/detail/recom-power/RD-0505D/2256316 | $7.33 | 1 | TRUE | FALSE | $7.50 |  |  | $14.83 | $311.74 | $121.87
 |  |  |  |  |  | FALSE | FALSE |  |  |  | $0.00 | $311.74 | $121.87
USB extenders for cameras | Ryan | USB3.1 M to F, 6ft | https://www.digikey.com/en/products/detail/CA-USB3-AM-AF-6FT/2057-CA-USB3-AM-AF-6FT-ND/9830219?itemSeq=343990845 | $21.93 | 1 | TRUE | FALSE |  | 2pack, shipping included |  | $21.93 | $289.81 | $121.87
 |  |  |  |  |  | FALSE | FALSE |  |  |  | $0.00 | $289.81 | $121.87
Joystick | Sid | PCB | https://jlcpcb.com/ | $4.00 | 1 | FALSE | FALSE |  |  |  | $4.00 | $289.81 | $121.87
Joystick | Sid | Cable Assemblies | https://www.digikey.com/en/products/detail/molex/0511100850-20-A-6-Z/8605283 | $11.20 | 2 | TRUE | FALSE |  |  |  | $22.40 | $267.41 | $121.87
Joystick | Sid | Cable Port Header | https://www.digikey.com/en/products/detail/te-connectivity-amp-connectors/2842126-4/10708958 | $0.46 | 2 | TRUE | FALSE |  |  |  | $0.92 | $266.49 | $121.87
Joystick | Sid | MUX | https://www.digikey.com/en/products/detail/texas-instruments/TMUX1574DYYR/11502304 | $0.72 | 1 | TRUE | FALSE |  |  |  | $0.72 | $265.77 | $121.87
Joystick | Sid | Digital Potentiometer | https://www.digikey.com/en/products/detail/analog-devices-inc/AD8402ARZ1-REEL/621147 | $5.01 | 1 | TRUE | FALSE |  |  |  | $5.01 | $260.76 | $121.87
 |  |  |  |  |  | FALSE | FALSE |  |  |  | $0.00 | $260.76 | $121.87
EStop | Dawson | Relay | https://www.digikey.com/en/products/detail/te-connectivity-potter-brumfield-relays/T92P7D12-12/365919 | $22.46 | 1 | TRUE | FALSE |  |  |  | $22.46 | $238.30 | $121.87
 |  |  |  |  |  | FALSE | FALSE |  |  |  | $0.00 | $238.30 | $121.87
 |  |  |  |  |  | FALSE | FALSE |  |  |  | $0.00 | $238.30 | $121.87
Joystick | Sid | digikey cart | https://www.digikey.com/short/jdtz2r1n | $23.98 | 1 | TRUE | FALSE | $40.00 | about 40 for 2 day shipping - trying to get parts here asap for sid |  | $63.98 | $174.32 | $121.87
User Input | Sid | USB hub w/ Ethernet | https://www.amazon.com/USB-Ethernet-Splitter-HUB-Network/dp/B07G8VZ51Z?hvadid=309707619534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 | $19.99 | 1 | TRUE | FALSE |  |  |  | $19.99 | $154.33 | $121.87
 |  |  |  |  |  | FALSE | FALSE |  |  |  | $0.00 | $154.33 | $121.87
Laptop Mount | Dawson | Laptop Bag | https://www.amazon.com/gp/product/B082LZFXMQ/ref=ox_sc_act_title_1?smid=A2NHPRCV0HF21K&psc=1 | $9.00 | 1 | TRUE | FALSE |  |  |  | $9.00 | $145.33 | $121.87
 |  |  |  |  |  | FALSE | FALSE |  |  |  | $0.00 | $145.33 | $121.87
 |  |  |  |  |  | FALSE | FALSE |  |  | start: | 500 | $145.33 | $121.87
 |  |  |  |  |  | FALSE | FALSE |  |  | sum: | $332.74 | $145.33 | $121.87
 |  |  |  |  |  | FALSE | FALSE |  |  | left: | $167.26 | $145.33 | $121.87
 |  |  |  |  |  | FALSE | FALSE |  |  |  | $0.00 | $145.33 | $121.87
 |  |  |  |  |  | FALSE | FALSE |  |  |  | $0.00 | $145.33 | $121.87
 |  |  |  |  |  | FALSE | FALSE |  |  |  | $0.00 | $145.33 | $121.87
 |  |  |  |  |  | FALSE | FALSE |  |  |  | $0.00 | $145.33 | $121.87
 |  |  |  |  |  | FALSE | FALSE |  |  |  | $0.00 | $145.33 | $121.87
 |  |  |  |  |  | FALSE | FALSE |  |  |  | $0.00 | $145.33 | $121.87
 |  |  |  |  |  | FALSE | FALSE |  |  |  | $0.00 | $145.33 | $121.87
 |  |  |  |  |  | FALSE | FALSE |  |  |  | $0.00 | $145.33 | $121.87
 |  |  |  |  |  | FALSE | FALSE |  |  |  | $0.00 | $145.33 | $121.87
 |  |  |  |  |  | FALSE | FALSE |  |  |  | $0.00 | $145.33 | $121.87
 |  |  |  |  |  | FALSE | FALSE |  |  |  | $0.00 | $145.33 | $121.87
 |  |  |  |  |  | FALSE | FALSE |  |  |  | $0.00 | $145.33 | $121.87
 |  |  |  |  |  | FALSE | FALSE |  |  |  | $0.00 | $145.33 | $121.87
 |  |  |  |  |  | FALSE | FALSE |  |  |  | $0.00 | $145.33 | $121.87
 |  |  |  |  |  | FALSE | FALSE |  |  |  | $0.00 | $145.33 | $121.87
 |  |  |  |  |  | FALSE | FALSE |  |  |  | $0.00 | $145.33 | $121.87

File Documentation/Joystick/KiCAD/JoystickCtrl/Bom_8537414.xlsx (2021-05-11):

Manufacturer Part Number | Manufacturer | Digi-Key Part Number | Customer Reference | Reference Designator | Packaging | Part Status | Quantity | Unit Price | Extended Price | Quantity Available | Mfg Std Lead Time | Description | RoHS Status | Lead Free Status | REACH Status
2842126-4 | TE Connectivity AMP Connectors | 17-2842126-4-ND |  |  | Tube | Active | 2 | 0.46 | $0.92 | 2786 | 18 Weeks | 8P,2MM,BRK HDR,DRVT,2.8,0.1AU,TB | Not Available | Not Available | Not Available
0511100850-20-A-6-Z | Molex | 0511100850-20-A-6-Z-ND |  |  | Bulk | Active | 2 | 11.2 | $22.40 | 50 | Not Available | 8 CIRC CABLE ASSY 20" Z | Not Available | Not Available | Not Available
TMUX1574DYYR | Texas Instruments | 296-TMUX1574DYYRCT-ND |  |  | Cut Tape (CT) | Active | 1 | 0.72 | $0.72 | 1619 | 6 Weeks | PRECISION ANALOG MULTIPLEXER | ROHS3 Compliant | Not Available | REACH Unaffected
AD8402ARZ1-REEL | Analog Devices Inc. | AD8402ARZ1-REELCT-ND |  |  | Cut Tape (CT) | Active | 1 | 5.01 | $5.01 | 2610 | 8 Weeks | IC DGTL POT 1KOHM 256TAP 14SOIC | ROHS3 Compliant | Lead free | REACH Unaffected

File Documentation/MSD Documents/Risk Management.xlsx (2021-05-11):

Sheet: Instructions
Instructions |  | Categories of Risk - these are examples of the sorts of risks that might fall into each category
Use this information to help you populate the Risk Management tab. The team and guide should discuss whether any additional information needs to be included. Beginning with the Systems Level Design Review, this document should be actively managed by the team, and discussed at each design review throughout MSD I and MSD II. As you approach the end of MSD II, your overall level of risk should approach, if not reach, 0. |  | Technical | Scope creep, components don't work as expected, team members lack the skills necessary to do the work, as-fabricated parts differ from design, flawed assumptions
 |  | Resource | Schedule (e.g.: parts don't come in on time, machine shop is busy), personnel (e.g.: team member gets sick, travels for an interview), cost (e.g.: components cost more than expected, fabrication must be outsourced), facilities (e.g.: specialized piece of equipment fails, lose access to lab)
 |  | Safety | Injury to team, injury to end user, damage to equipment
 |  | Environmental | Team must dispose of significant excess material, design requires hazardou materials, selecting a low-cost component that could lead to shorter life and the need for additional purchases, design requires purchase of consummable items for end user
 |  | Social | Design choices cause harm to a team member or end user based on social issues (e.g.: loss of confidentiality, contradicts local cultures and customs)
Likelihood scale | Severity scale | “Importance Score” (Likelihood x Severity) – use this to guide your preference for a risk management strategy
1 - This cause is unlikely to happen | 1 - The impact on the project is very minor. We will still meet deliverables on time and within budget, but it will cause extra work. | Prevent | Action will be taken to prevent the cause(s) from occurring in the first place.
2 - This cause could conceivably happen | 2 - The impact on the project is noticeable. We will deliver reduced functionality, go over budget, or fail to meet some of our requirements. | Reduce | Action will be taken to reduce the likelihood of the cause and/or the severity of the effect on the project, should the cause occur
3 - This cause is very likely to happen | 3 - The impact on the project is severe. We will not be able to deliver, or what we deliver will not meet the customer's needs. | Transfer | Action will be taken to transfer the risk to something else. Insurance is an example of this. You purchase an insurance policy that contractually binds an insurance company to pay for your loss in the event of accident. This transfers the financial consequences of the accident to someone else. Your car is still a wreck, of course.
 |  | Accept | Low importance risks may not justify any action at all. If they happen, you simply accept the consequences.

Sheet: Risk Management
Team #: | P21311 | Team Name: | Mind Controlled Wheelchair
Date: | 2021-02-28 | Document Owner: | Dawson Hilk
Revision #: | 1
 |  |  |  |  | 1,3,9 | 1,3,9
ID | Category | Risk Item | Effect | Cause | Likelihood | Severity | Importance | Action to Minimize Risk | Owner
 | What type of risk is this? | Describe the risk briefly | What is the effect on any or all of the project deliverables if the cause actually happens? | What are the possible cause(s) of this risk? | L | S | L*S | What action(s) will you take (and by when) to prevent, reduce the impact of, and/or transfer the risk of this occurring? | Who is responsible for following through on mitigation?
1 | safety, environmental | The chair could slam into walls. | Time delay to recode | Did not code correctly | 9 | 1 | 9 | Code it right the first time
2 | safety | The user could fall down stairs if we don't code it correctly | Hospitalized user = closed project | Did not code correctly | 1 | 9 | 9 | Code it right the first time
3 | safety | The chair could catch fire from an overheating CPU(cooling) | Would need new CPU or new chair, pushing back deliverable | Did not take in account how hot the CPU might become | 1 | 9 | 9 | Monitoring CPU and doing proper research before hand
4 | safety | What if the user falls out of chair or isn't on board | Hurt user or rogue chair that would need to be coded | Did not code correctly or establish enough safety restraints | 1 | 3 | 3 | Brainstorm ideas to see if we need it or code it
5 | technical | Interface with camera could be troubling and lead to many unforseen issues | Data from camera would need to be trimmed down and less information is gained | Camera output not as expected or behaiving unexpectedly | 3 | 3 | 9 | Test and understand fully the camera outputs and correlation to the world and what calculations need to be done to make it workable
6 | technical | Software to map could be very complex | Maps would need to be thrown out or adapted to be less descript | Mapping data is too large or too complex to keep good data of | 3 | 1 | 3 | Test to understand how camera information is tuned into maps and what calaculations/storage needs to happen
7 | technical | The interface with the chair controls could be unweildy and not be consistent | More testing on how to control the chair and how the chair reacts to inputs would be needed | Chair responds in unwanted or unexpected ways to input | 1 | 1 | 1 | Careful usage of controls and testing to know how they reacts to all combination on inputs
8 | technical | The software to make heading decisions for chair could have many corner cases that lead to catastrophic failures | Corner cases would need to be worked out, time lost | chair makes incorrect or dangerous heading decisions | 9 | 9 | 81 | Document well and test all code for possible scenarios
9 | safety/environment/resource | Campus closing | Project becomes entirely remote | health concerns | 3 | 9 | 27 | Health saftey
10 | resource | we will need a high quality motherboard to execute the path planning algorithms | Path planning is slowed, potentially lagging the user | Lack of research and/or funding | 3 | 3 | 9 | Do more research before deciding on motherboard
11 | technical | the computing done on the cameras is not as much as we would have hoped | More computing in the motherboard, which may not be able to handle it | Lack of research | 1 | 3 | 3 | Do more research before deciding on motherboard
12 | social | We leave out an important feature that a quadriplegic individual would require. | Dis-satisfaction from the end-user | Inability to conduct an interview | 3 | 1 | 3 | Research what we would have interviewed
13 | safety/technical | Chair does not come to a full stop if object in path | Damage to chair | Did not code correctly | 1 | 9 | 9 | Code it correct first and recheck code imediately if issue arises
14 | safety/technical | Over-correction when faces with obstacles | Hurt user or rogue chair | Did not code correctly or camera output issues | 3 | 9 | 27 | Code it correct first and check to ensure cameras dont move
15 | technical/environmental | Lighting with negatively affect the cameras | Inacturate/inconsistant mapping recorded | Lights | 9 | 1 | 9 | Test how lights effect camera prior to implementation
16 | technical | Camera will be bumped/moved | Inacturate/inconsistant mapping recorded, damage to resources | People walking past, objects hit | 9 | 3 | 27 | Securely mount cameras so they cannot move vertically or horizontally
17 | resource | The chair that we have will not be sufficient for what we want to do | Resource and redesign mounting and functionality | Battery, programability, etc. insufficient for our needs | 1 | 3 | 3 | Look at all components early on and determine if anything needs to be changed or added
18
19
20

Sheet: Risk V2
Team #: |  | P21311 | Team Name: | Mind Controlled Wheelchair
Date: |  | 2021-02-28 | Document Owner: | Dawson Hilk
Revision #: |  | 4
 |  |  |  |  |  | 1,3,9 | 1,3,9
ID | State | Category | Risk Item | Effect | Cause | Likelihood | Severity | Importance | Action to Minimize Risk | Owner
 | active | What type of risk is this? | Describe the risk briefly | What is the effect on any or all of the project deliverables if the cause actually happens? | What are the possible cause(s) of this risk? | L | S | L*S | What action(s) will you take (and by when) to prevent, reduce the impact of, and/or transfer the risk of this occurring? | Who is responsible for following through on mitigation?
8 | active | technical | The software to make heading decisions for chair could have many corner cases that lead to catastrophic failures | Corner cases would need to be worked out, time lost | chair makes incorrect or dangerous heading decisions | 9 | 9 | 81 | Document well and test all code for possible scenarios - accept that we may not hit all cases by may
5 | accepted risk | technical | Interface with camera could be troubling and lead to many unforseen issues | Data from camera would need to be trimmed down and less information is gained | Camera output not as expected or behaiving unexpectedly | 9 | 9 | 81 | Test and understand fully the camera outputs and correlation to the world and what calculations need to be done to make it workable
19 | accepted risk | technical | T265 SDK compatanbility, unstable with current version 2.41 - last documented working version was 2.31 | T265 camera could be unusable, loss of localization and mapping | Realsesne SDK issues | 9 | 9 | 81 | try downgrading SDK, adjust goal from complete automation back to pure object avoidance
7 | closed | technical | The interface with the chair controls could be unweildy and not be consistent | More testing on how to control the chair and how the chair reacts to inputs would be needed | Chair responds in unwanted or unexpected ways to input | 9 | 3 | 27 | Implement Physical joystick controller
9 | active | safety/environment/resource | Campus closing | Project becomes entirely remote | health concerns | 9 | 3 | 27 | Health saftey
14 | active | safety/technical | Over-correction when faced with obstacles | Hurt user or rogue chair | Did not code correctly or camera output issues | 3 | 9 | 27 | Start testing in open space, introduce object and verify avoidance turns before doing actual run.
1 | active | safety, environmental | The chair could slam into walls. | Time delay to recode | Did not code correctly | 9 | 1 | 9 | Test first in an open area and introduce "mock walls" such as a solid flat object and see how chair reacts first before introducing it to an actual wall
15 | active | technical/environmental | Lighting with negatively affect the cameras | Inacturate/inconsistant mapping recorded | Lights | 9 | 1 | 9 | Move cameras back more for shading
16 | active | technical | Camera will be bumped/moved | Inacturate/inconsistant mapping recorded, damage to resources | People walking past, objects hit | 3 | 3 | 9 | Replace velcro with bolts
3 | closed | safety | The chair could catch fire from an overheating CPU(cooling) | Would need new CPU or new chair, pushing back deliverable | Did not take in account how hot the CPU might become | 1 | 9 | 9 | Monitoring CPU and doing proper research before hand
2 | active | safety | The user could fall down stairs if we don't code it correctly | Hospitalized user = closed project | Did not code correctly | 1 | 9 | 9 | Stay away from ledges until general movement is verified, then view how ledges are seen with the chair not moving and then introduce detecting while in motion
13 | active | safety/technical | Chair does not come to a full stop if object in path | Damage to chair | Did not code correctly | 1 | 9 | 9 | Check first with a soft object or easily movable object (holding meter stick in view) to see how chair reacts, then move to stationary objects that would commonly be found
12 | closed | social | We leave out an important feature that a quadriplegic individual would require. | Dis-satisfaction from the end-user | Inability to conduct an interview | 3 | 1 | 3 | Research what we would have interviewed
4 | closed | safety | What if the user falls out of chair or isn't on board | Hurt user or rogue chair that would need to be coded | Did not code correctly or establish enough safety restraints | 1 | 3 | 3 | Brainstorm ideas to see if we need it or code it
6 | triggered | technical | Software to map could be very complex | Maps would need to be thrown out or adapted to be less descript | Mapping data is too large or too complex to keep good data of | 9 | 1 | 9 | Test to understand how camera information is turned into maps and what calaculations/storage needs to happen
11 | closed | technical | the computing done on the cameras is not as much as we would have hoped | More computing in the motherboard, which may not be able to handle it | Lack of research | 1 | 3 | 3 | Do more research before deciding on motherboard
17 | closed | resource | The chair that we have will not be sufficient for what we want to do | Resource and redesign mounting and functionality | Battery, programability, etc. insufficient for our needs | 1 | 3 | 3 | Look at all components early on and determine if anything needs to be changed or added
18 | closed | safety | overheating Raspberry Pi (cooling) | Would need better cooling system in RasPi Case | Did not take in account how hot the Pi might become | 1 | 3 | 3 | Adding cooling fan and possible heat sinc
10 | active | resource | we will need a high quality motherboard to execute the path planning algorithms | Path planning is slowed, potentially lagging the user | Lack of research and/or funding | 1 | 3 | 3 | Do more research before deciding on motherboard
20 | triggered | technical | PCB design doesn't allow for desired functionality | requires purchase of new design / prototype | lack of prior research | 9 | 3 | 27
21 | active | technical | integrating ethernet code (python) with camera scripts (C) | Inability to communicate with headset | difference in language | 3 | 1 | 3 | Work towards calling python in C or implement in C
22 | active | technical | too much drift in IMU readings. | Loss of localization. Difficult to find next intersection | depricated cameras | 3 | 9 | 27 | Talk to customer to compromize between devices
23 | active | technical/safety | Too much latency between detecting an object (moving quickly) and determining new path | Cannot turn quick enough to avoid obstacles | inefficient coding | 3 | 3 | 9 | slow down to allow object to pass by; no path alteration
24

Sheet: risks ordered
Risks | Likelihood | Severity | Importance
 | L | S | L*S
The software to make heading decisions for chair could have many corner cases that lead to catastrophic failures | 9 | 9 | 81
Camera will be bumped/moved | 9 | 3 | 27
Campus closing | 3 | 9 | 27
Over-correction when faces with obstacles | 3 | 9 | 27
The chair could slam into walls. | 9 | 1 | 9
Lighting with negatively affect the cameras | 9 | 1 | 9
Interface with camera could be troubling and lead to many unforseen issues | 3 | 3 | 9
we will need a high quality motherboard to execute the path planning algorithms | 3 | 3 | 9
The user could fall down stairs if we don't code it correctly | 1 | 9 | 9
The chair could catch fire from an overheating CPU(cooling) | 1 | 9 | 9
Chair does not come to a full stop if object in path | 1 | 9 | 9
Software to map could be very complex | 3 | 1 | 3
We leave out an important feature that a quadriplegic individual would require. | 3 | 1 | 3
The chair that we have will not be sufficient for what we want to do | 1 | 3 | 3
What if the user falls out of chair or isn't on board | 1 | 3 | 3
the computing done on the cameras is not as much as we would have hoped | 1 | 3 | 3
The interface with the chair controls could be unweildy and not be consistent | 1 | 1 | 1

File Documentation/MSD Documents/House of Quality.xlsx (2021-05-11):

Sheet: Cust Rqmts
Team #: | P21311 | Team Name: | Mind Controlled Wheelchair
Date: | 2021-05-05 | Document Owner: | Ryan Radicello
Revision #: | 3
Customer Rqmt. # | Importance | Requirement | Comments/Status | Satisfied | Comments/Status
CR1 | 9 | Max speed is average walking speed
CR2 | 9 | Chair must have emergency stop button (cuts power) |  | X
CR3 | 9 | Remember previously mapped areas | Two areas is fine | X
CR4 | 9 | Explore an area to pre-map it (can be pushed manually) |  | X
CR5 | 9 | Label areas of mapped locations | can be done after-the-fact | X
CR6 | 9 | In a pre-mapped space, navigate to a selected destination |  | X | No turn at node
CR7 | 9 | avoid stationary objects (walls) |  | X
CR8 | 9 | For full auto-navigation, allow user to start & stop |  |  | User Start
CR9 | 3 | Travel through doorways without user assistance | Higher priority than other 3's |  | If large doorways
CR10 | 3 | Receive little input from user device to determine heading |  | X
CR11 | 3 | Input based on 3 cmds (start/stop, left, right)
CR12 | 3 | Slows down in crowded environment |  | X
CR13 | 3 | Identifies and waits for input at desicion points
CR14 | 3 | Avoid Moving objects (pedestrians) |  | X
CR15 | 3 | Detect stairs or ledges, AVOID THEM
CR16 | 3 | Map unknown areas "on-the-fly"
CR17 | 1 | Chair battery lasts a day
CR18 | 1 | Stay on the right side of the hallway |  |  | Too well
CR19 | 1 | Recognize new area due to elevator (vertical motion) | Per custustomer "would be nice but not requiered"
CR20 | 1 | Pre-map space autonomously
Cust. Rqmt. #: enables cross-referencing (traceability) with engineering requirements
Importance: HIGH=must have, MEDIUM=nice to have, LOW=preference only.
Description: organize as primary and secondary requirements (hierarchy) -- Ulrich exhibit 4.8
Comment/Status: allows tracking of questions, proposed changes, etc; indicate if you are meeting the requirement ("met") or not ("not met")

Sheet: Eng Rqmts
Team #: | P21311 | Team Name: | Mind Controlled Wheelchair
Date: | 2021-05-05 | Document Owner: | Cheyenne Dailey
Revision #: | 4
rqmt. # | Importance | Source | Function | Engr. Requirement (metric) | Unit of Measure | Marginal Value | Ideal Value | Actual Value | Test Result | Direction of Improvement | Comments/Status | Test Number
ER1 | 9 | CR1 | Performance | Max Speed | meters per second | 1 | 1.4
ER2 | 9 | CR7 | Performance/Safety | Stationary Object detection | meters | 1 | 2
ER3 | 9 | CR4,CR7,CR14 | Performance | Camera visibility range | degrees | 125 | 180
ER4 | 9 | CR7, CR9 | Performance/Safety | Stationary Object Avoidance | yes/no | yes | yes
ER5 | 9 | CR2 | Safety/Usability | Accessibility/Visibility of Emergency Stop Buttons | meters | 0.5 | 1 |  |  |  | Can see ESB from x meters away
ER6 | 9 | CR9 | Usability | Chair width with cameras | meters | 0.7 | 0.6
ER7 | 9 | CR13 | Usability | Registers different path options | yes/no | no | yes
ER8 | 9 | CR11,CR10,CR8 | Usability | User Input Delay | seconds | 4 | 3
ER9 | 9 | CR3 | Performance | Maps Stored | # of maps | 1 | 3
ER10 | 9 | CR5 | Usability/Performance | Label locations | yes/no | yes | yes
ER11 | 3 | CR12 | Saftey/Performance | Slow speed in congested areas | meters per second | 0.5 | 0.45 |  |  |  | 1 mph = ~0.45 m/s
ER12 | 3 | CR18,CR7 | Usability | Distance threshold from walls | meters | 1 | 0.75
ER13 | 3 | CR14 | Performance/Safety | Moving Object Detection | meters | 1 | 2
ER14 | 3 | CR14 | Performance/Safety | Moving Object Avoidance | yes/no | no | yes
ER15 | 3 | CR15 | Performance/Safety | Ledge Detection | meters | 1 | 2
ER16 | 3 | CR1, CR12 | Performance | Joystick CTRLR Min Output Voltage | Volts | -1 | -1.25
ER17 | 3 | CR1, CR12 | Performance | Joystick CTRLR Max Output Voltage | Volts | 1 | 1.25
ER18 | 1 | CR1 | Performance | Max Speed Modes | # speed modes | 1 | >1
ER19 | 1 | CR17 | Performance | Battery Capacity | Amp-hours | 10 | 15
ER20 | 1 | CR17 | Performance | Battery Endurance | hours | 8 | 16
ER21 | 3 | CR2 | Saftey | E-stop Btn. Case Force Capability | Newtons | ? | ?
ER22 | 3 | CR1, CR12 | Usability/Safety | Ras-Pi to Arduino CMD Freq | CMDs per sec | 5 | 10
ER23
Rqmt. #: enables cross-referencing (traceability) and allows mapping to lower level requirements within separate documents
Source: Customer requirement #, regulatory standard (eg. EN 60601), and/or "implied" (must exist but doesn't have an associated customer rqmt), constraint
Description: quantitative, measureable, testable details
TEST RESULT KEY |  |  |  |  | DIRECTION OF IMPROVEMENT KEY
X | Does not meet expectation |  |  |  | X | Must be within a specified range.
Δ | Caution-Undetermined if specification is met |  |  |  | ↑ | Improvement occurs with increasing test value.
O | Meets specification |  |  |  | ↓ | Improvement occurs with decreasing test value.

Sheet: Cust vs Eng Rqmts
Team # | P21311 | Team Name | Mind Controlled Wheelchair
Date | 2021-05-05 | Document Owner | Dawson
Version # | 2
 |  |  | Engineering Requirements
 |  | Engineering Requirement # | ER1 | ER2 | ER3 | ER4 | ER5 | ER6 | ER7 | ER8 | ER9 | ER10 | ER11 | ER12 | ER13 | ER14 | ER15 | ER16 | ER17 | ER18 | ER19 | ER20 | ER21 | ER22
Customer Requirements | Customer Requirement # | Engineering Capabilities > Customer Requirements v | Max Speed | Stationary Object detection | Camera visibility range | Stationary Object Avoidance | Accessibility/Visibility of Emergency Stop Buttons | Chair width with cameras | Registers different path options | User Input Delay | Maps Stored | Label locations | Slow speed in congested areas | Distance threshold from walls | Moving Object Detection | Moving Object Avoidance | Ledge Detection | Joystick CTLR Min Output Voltage | Joystick CTLR Max Output Voltage | Max Speed Modes | Battery Capacity | Battery Endurance | E-stop Case Strength | Ras-Pi to Arduino CMD freq
 | CR1 | Max speed is average walking speed | X |  |  |  |  |  |  |  |  |  |  |  |  |  |  | X | X | X |  |  |  | X
 | CR2 | Chair must have emergency stop button (cuts power) |  |  |  |  | X |  |  |  |  |  |  |  |  |  |  |  |  |  |  |  | X
 | CR3 | Remember previously mapped areas |  |  |  |  |  |  |  |  | X
 | CR4 | Explore an area to pre-map it (can be pushed manually) |  |  | X
 | CR5 | Label areas of mapped locations |  |  |  |  |  |  |  |  |  | X
 | CR6 | In a pre-mapped space, navigate to a selected destination
 | CR7 | avoid stationary objects (walls) |  | X | X | X |  |  |  | X |  |  |  | X
 | CR8 | For full auto-navigation, allow user to start & stop
 | CR9 | Travel through doorways without user assistance |  |  |  | X |  | X
 | CR10 | Receive little input from user device to determine heading |  |  |  |  |  |  |  | X
 | CR11 | Input based on 3 cmds (start/stop, left, right) |  |  |  |  |  |  |  | X
 | CR12 | Slows down in crowded environment |  |  |  |  |  |  |  |  |  |  | X |  |  |  |  | X | X |  |  |  |  | X
 | CR13 | Identifies and waits for input at desicion points |  |  |  |  |  |  | X
 | CR14 | Avoid Moving objects (pedestrians) |  |  | X |  |  |  |  |  |  |  |  |  | X | X
 | CR15 | Detect stairs or ledges, AVOID THEM |  |  |  |  |  |  |  |  |  |  |  |  |  |  | X
 | CR16 | Map unknown areas "on-the-fly"
 | CR17 | Chair battery lasts a day |  |  |  |  |  |  |  |  |  |  |  |  |  |  |  |  |  |  | X | X
 | CR18 | Stay on the right side of the hallway |  |  |  |  |  |  |  |  |  |  |  | X
 | CR19 | Recognize new area due to elevator (vertical motion)
 | CR20 | Pre-map space autonomously
Technical Targets |  |  | Pounds | # of speed modes | ft/s | yes/no | # of plugs | Amp-hours | Voltage & amp-hours | yes/no | Dollars | yes/no | yes/no | # of terrains | Degrees | yes/no | Percentage | Percentage | yes/no | yes/no | feet | seconds
Technical Benchmarking |  | 5 (Best)
 |  | 4
 |  | 3
 |  | 2
 |  | 1
Raw Score
Relative Weightage
 |  | old document (9/3/2020)
Team # | P21311 | Team Name | Mind Controlled Wheelchair
Date | 2020-09-03 | Document Owner | Dawson
Version # | 1
 |  |  | Engineering Requirements
 |  | Engineering Requirement # | ER1 | ER2 | ER3 | ER4 | ER5 | ER6 | ER7 | ER8 | ER9 | ER10 | ER11 | ER12 | ER13 | ER14 | ER15 | ER16 | ER17 |  |  |  |  | ER18 | ER19 | ER20
Customer Requirements | Customer Requirement # | Engineering Capabilities > Customer Requirements v |  |  |  |  |  |  |  |  |  |  | #REF! |  | #REF! |  |  |  | #REF! |  |  |  |  |  |  | #REF!
 | CR1 | #REF! |  |  |  |  |  |  |  |  |  |  | x |  | x
 | CR2 | #REF!
 | CR3
 | CR4 |  |  |  |  |  | x |  |  | x
 | CR5 | #REF!
 | CR6 |  |  |  |  |  |  |  |  |  |  | x
 | CR7 |  | x | x
 | CR8 |  |  |  | x |  |  |  | x
 | CR9 |  |  |  |  |  |  |  |  |  | x
 | CR10 |  |  |  | x | x | x
 | CR11 |  |  |  |  |  |  | x
 | CR12 |  |  |  | x | x
 | CR13 |  |  |  |  |  |  |  |  |  |  |  |  | x
 | CR14 |  |  |  |  |  |  |  |  |  |  |  |  |  |  |  | x
 | CR15
 | CR16 |  |  |  |  | x
 | CR17 |  |  |  |  |  |  |  |  |  |  |  |  |  |  |  |  | x
 | CR18 |  |  |  |  | x |  |  |  |  |  |  |  |  |  | x
 | CR19
 | CR20 | #REF! |  |  |  |  |  |  |  |  |  |  | x |  | x
 | CR21
 | CR22
Technical Targets |  |  | Pounds | # of speed modes | ft/s | yes/no | # of plugs | Amp-hours | Voltage & amp-hours | yes/no | Dollars | yes/no | yes/no | # of terrains | Degrees | yes/no | Percentage | Percentage | yes/no |  |  |  |  | yes/no | feet | seconds
Technical Benchmarking |  | 5 (Best)
 |  | 4
 |  | 3
 |  | 2
 |  | 1
Raw Score
Relative Weightage

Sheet: Sample Test Plan
Team #: | P00000 | Team Name: | Sample MSD Project
Date: | 2021-05-05 | Document Owner: | Team Member
Revision #: | 1
Subsystem/ Function/ Feature Name: |  |  | Volume Sensitivity Testing
Date of Test: | 2013-11-05
Performed By: __Steve DiGerardo, Paulina Klimkiewicz, Matt Burkell and David Herdzik___
Tested By: __Steve DiGerardo, Paulina Klimkiewicz, Matt Burkell and David Herdzik___
Concluded Condition of meeting Engineering Specification |  |  |  | Ο- Meets Marginal Value
I. TESTING SPECIFICATION
Specification Number | Importance | Source | Function | Specification (Metric) | Unit of Measure | Marginal Value | Ideal Value | Comments/Status
S1 | 1 | PRP | System | Volume Control | Liters | 0.2 ± 0.2
II. EQUIPMENT REQURIED
Specification Number | Equipment or Instrumentation required
S1 | Fully Charged Battery, Pump, Differential and Pressure Sensor Unit, Digital Mass Flow sensor
III. DATA COLLECTION STRATEGY
Specification Number | Data acquisition strategy
S1 | The goal of this test is to characterize our sensors to the appropriate flow rate as seen by the digital mass flow rate sensor. By calibrating our sensor unit to the sensitivity of the digital flow sensor, our venturi system design will be able to provide that sensitivity when in operation.
III. TESTING FLOWCHART
IV. RAW DATA ACQUISITION
Volume Testing: System Configuartion with stop watch testing Using a .7 time multiplier | Flow Rate (l/s) | Flow rate (l/s) | Time (s) | Volume (l) | Volume Comanded (l) | % Diff
 | 15 | 0.25 | 3.9 | 0.975 | 1.02 | -4.411764706%
 | 15 | 0.25 | 4 | 1 | 1.02 | -1.960784314%
 | 15 | 0.25 | 3.9 | 0.975 | 1.02 | -4.411764706%
 | 15 | 0.25 | 4.1 | 1.025 | 1.02 | 0.4901960784%
 | 30 | 0.5 | 4 | 2 | 2.03 | -1.477832512%
 | 30 | 0.5 | 4.1 | 2.05 | 2.03 | 0.9852216749%
 | 30 | 0.5 | 4.1 | 2.05 | 2.03 | 0.9852216749%
 | 30 | 0.5 | 4 | 2 | 2.03 | -1.477832512%
V. RESULTS
VI. CONCLUSION
In this test, we are confirming the accuracy of our breath delivery system to ensure it meets volume sensitivity. In this test, at different flow rates, we are comparing the amount of flow given by the pump to the amount of flow as read by a digital sensor. From the test points above we test a lower range flow of 15 L/min and a higher range flow of 30 L/min. In each of the flow domains we are able to read similar data to that of the digital mass flow sensor. Our maximum error experienced is 4%. This is well under the 10% sensitivity flow desired. Thus we can conclude that our pump performance and sensing capabilites are able to sense the the flow accurately.

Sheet: S1 Test Plan
Team #: | P00000 | Team Name: | Sample MSD Project
Date: | 2021-05-05 | Document Owner: | Team Member
Revision #: | 1
Subsystem/ Function/ Feature Name:
Date of Test:
Performed By:
Tested By:
Concluded Condition of meeting Engineering Specification:
I. TESTING SPECIFICATION
Specification Number | Importance | Source | Function | Specification (Metric) | Unit of Measure | Marginal Value | Ideal Value | Comments/Status
S1
II. EQUIPMENT REQURIED
Specification Number | Equipment or Instrumentation required
S1
III. DATA COLLECTION STRATEGY
Specification Number | Data acquisition strategy
S1
III. TESTING FLOWCHART
IV. RAW DATA ACQUISITION
V. RESULTS
VI. CONCLUSION

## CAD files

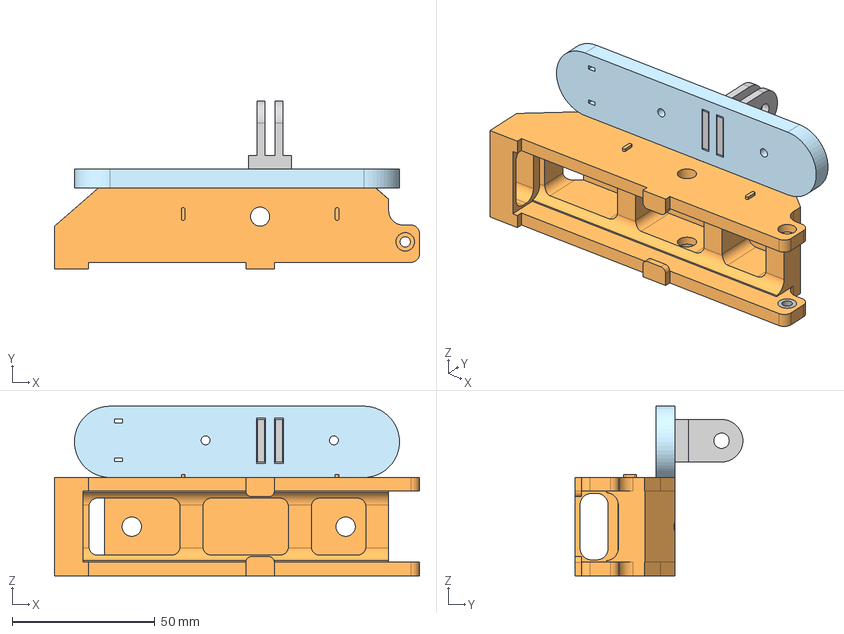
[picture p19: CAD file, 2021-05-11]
Documentation/3D Models/CameraAssembly/CameraAssembly.step
128.0 x 58.9 x 59.5 mm
GoPro Hinge
D435 mount
T165 Mount

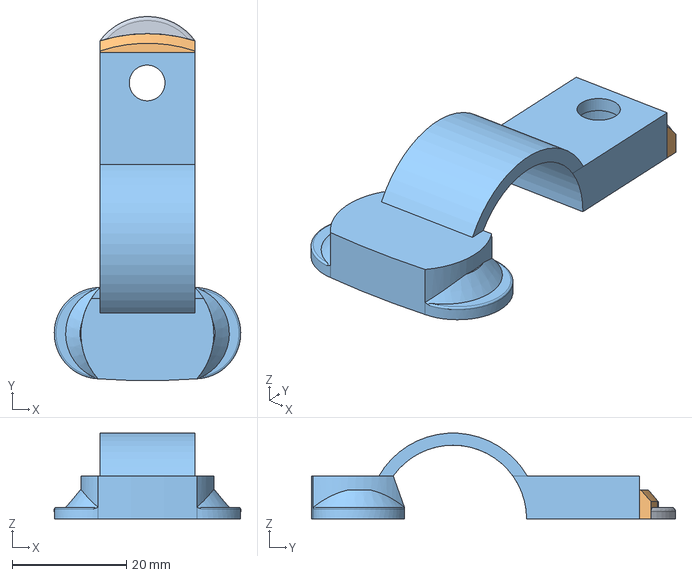
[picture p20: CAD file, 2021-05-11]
Documentation/3D Models/Footrest2CameraMount/Footrest2CameraMount.step
32.6 x 63.7 x 15.0 mm

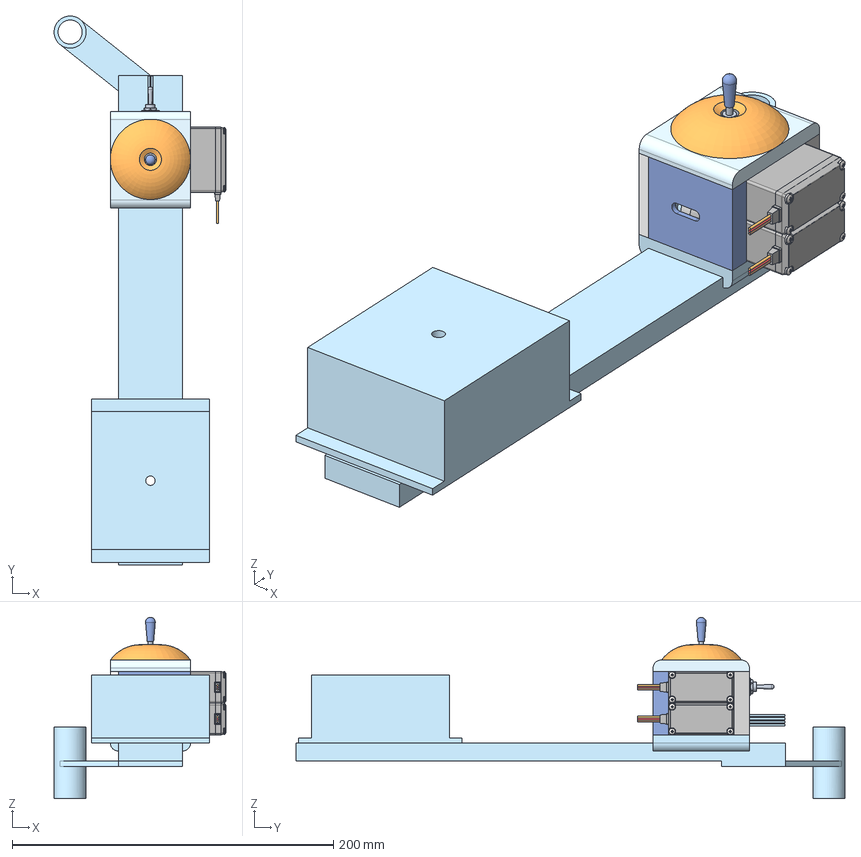
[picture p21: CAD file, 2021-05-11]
Documentation/3D Models/JoystickCtrlV3/JoystickCtrlV3.step
107.0 x 341.8 x 112.8 mm
POT x 2
ServoPotCoupling x 2
Joystick Stick
Joystick Plate
Proto Mount
Servo Rack Front
Base
Servo Rack Back
Joystick Cover
M6x0.5 Hex Nut
SPDT Toggle Switch Treaded Tube x 2
SPDT Toggle Switch Pin
AS 1969 (Internal Tooth Lock Washer Type A) M6
Toggle Switch x 2
SPDT Toggle Switch Base
SPDT Toggle Switch Anti-Rotation Washer
SPDT Toggle Switch Pin_2
M6x0.5 Hex Nut_1
SPDT Toggle Switch Pin_1
Bolt
pan cross head_am_B18.6.7M - M2 x 0.4 x 3 Type I Cross Recessed PHMS --3N x 8
TOWER PRO MG-995, ANALOG SERVO, CONNECTOR x 6
TOWER PRO MG-995, ANALOG SERVO, BODY, TOP x 2
TOWER PRO MG-995, ANALOG SERVO, BODY, BOTTOM x 2
TOWER PRO MG-995, ANALOG SERVO, SHAFT x 2
TOWER PRO MG-995, ANALOG SERVO, BODY, MIDDLE x 2
Chair Arm

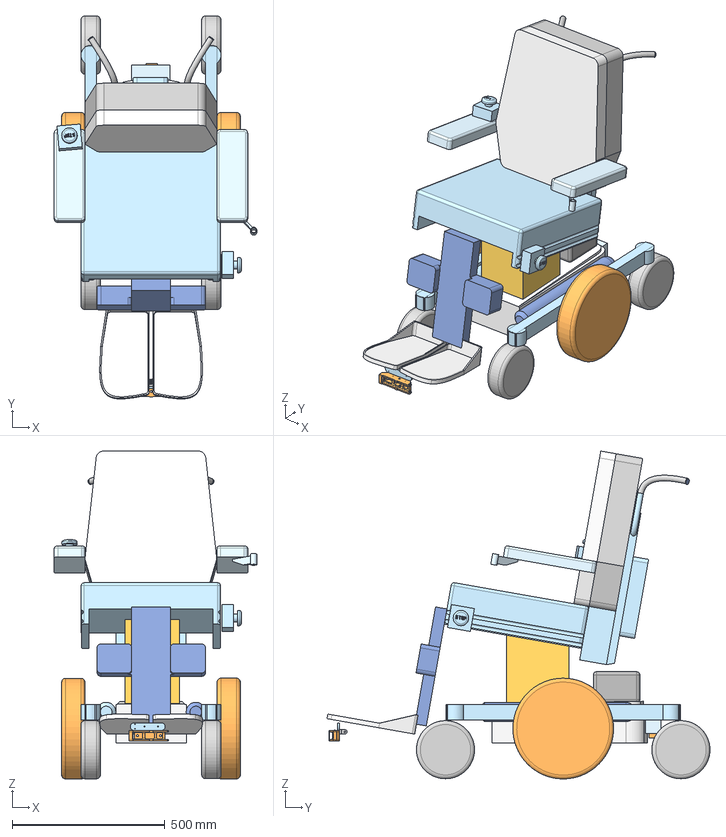
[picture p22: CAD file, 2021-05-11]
Documentation/3D Models/WheelchairModel.step
663.8 x 1254.7 x 1074.2 mm
Surface 1
Surface 2

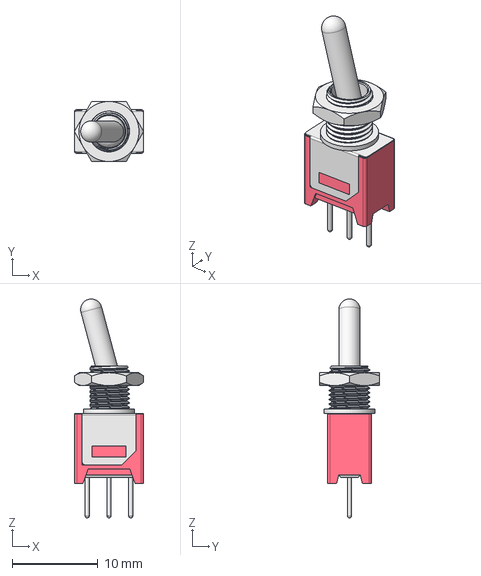
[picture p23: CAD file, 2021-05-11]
Documentation/Joystick/KiCAD/JoystickCtrl/3D models/200-MSP-1-T3-B1-M2-PE-rev2.step
8.10 x 7.00 x 25.5 mm

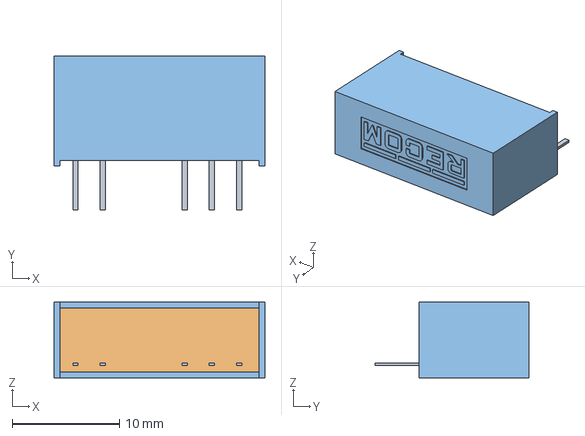
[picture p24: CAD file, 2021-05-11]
Documentation/Joystick/KiCAD/JoystickCtrl/local_lib/RD-0505D/RD-0505D.step
19.6 x 14.3 x 7.05 mm

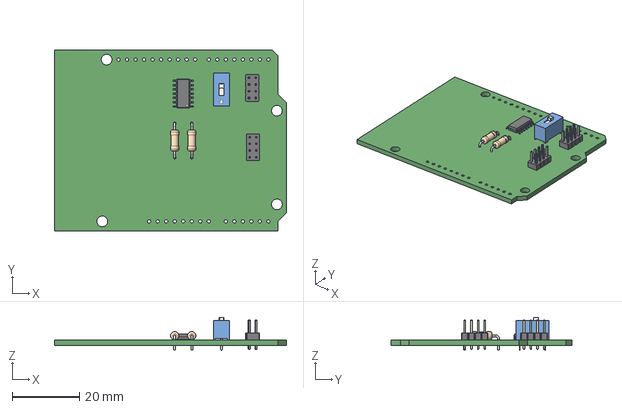
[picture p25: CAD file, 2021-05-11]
Documentation/Joystick/KiCAD/JoystickCtrl/3D models/JoystickCtrl.step
69.2 x 54.0 x 9.95 mm

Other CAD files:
Documentation/3D Models/Footrest2CameraMount/Footrest2CameraMount.stl

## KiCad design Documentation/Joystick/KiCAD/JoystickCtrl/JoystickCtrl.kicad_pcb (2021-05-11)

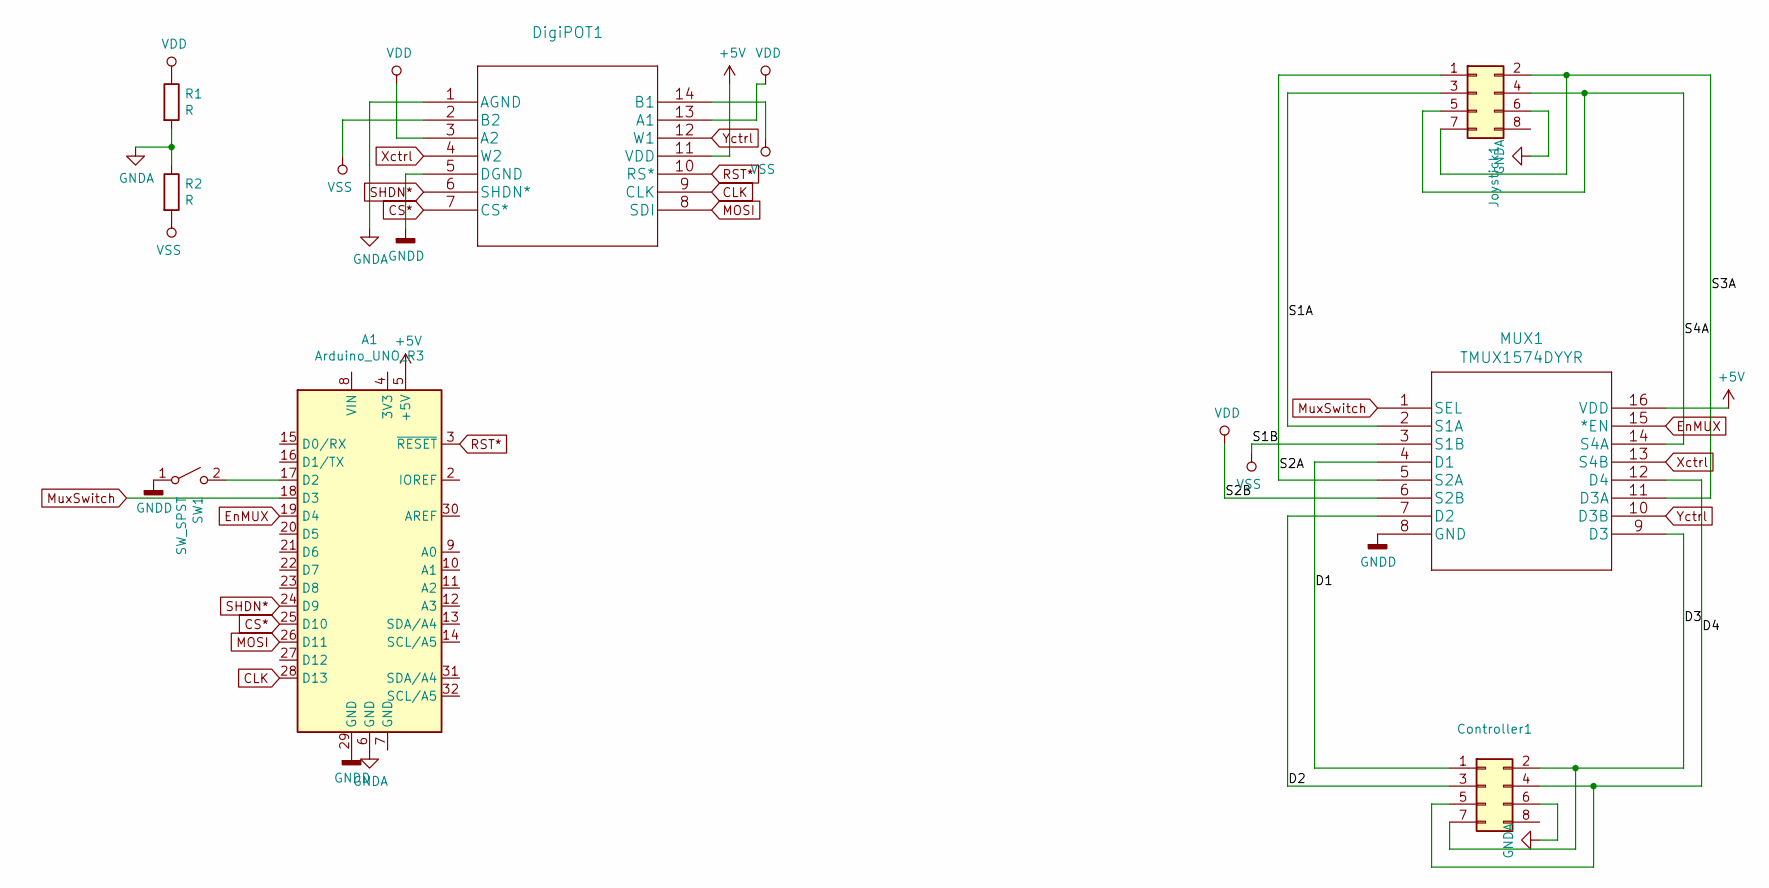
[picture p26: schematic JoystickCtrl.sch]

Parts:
A1: Arduino_UNO_R3; Arduino_UNO_R3_WithMountingHoles
Controller1: Conn_02x04_Odd_Even; PinHeader_2x04_P2.00mm_Vertical
DigiPOT1: AD8402ARZ1-REEL; SOIC-14_3.9x8.7mm_P1.27mm
Joystick1: Conn_02x04_Odd_Even; PinHeader_2x04_P2.00mm_Vertical
MUX1: TMUX1574DYYR
R1, R2: R; R_Axial_DIN0207_L6.3mm_D2.5mm_P10.16mm_Horizontal
SW1: SW_SPST; SW_DIP_SPSTx01_Slide_9.78x4.72mm_W7.62mm_P2.54mm

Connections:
+5V: A1.5 (+5V), DigiPOT1.11 (VDD), MUX1.16 (VDD)
/D1: Controller1.1, MUX1.4 (D1)
/D2: Controller1.3, MUX1.7 (D2)
/D3: Controller1.2, Controller1.7, MUX1.9 (D3)
/D4: Controller1.4, Controller1.5, MUX1.12 (D4)
/S1A: Joystick1.3, MUX1.2 (S1A)
/S2A: Joystick1.1, MUX1.5 (S2A)
/S3A: Joystick1.2, Joystick1.7, MUX1.11 (D3A)
/S4A: Joystick1.4, Joystick1.5, MUX1.14 (S4A)
CLK: A1.28 (D13), DigiPOT1.9 (CLK)
CS*: A1.25 (D10), DigiPOT1.7 (CS*)
EnMUX: A1.19 (D4), MUX1.15 (*EN)
GNDA: A1.6 (GND), Controller1.6, DigiPOT1.1 (AGND), Joystick1.6, R1.2, R2.1
GNDD: A1.29 (GND), DigiPOT1.5 (DGND), MUX1.8 (GND), SW1.1 (A)
MOSI: A1.26 (D11), DigiPOT1.8 (SDI)
MuxSwitch: A1.18 (D3), MUX1.1 (SEL)
unnamed: A1.17 (D2), SW1.2 (B)
RST*: A1.3 (~RESET), DigiPOT1.10 (RS*)
SHDN*: A1.24 (D9), DigiPOT1.6 (SHDN*)
VDD: DigiPOT1.3 (A2), DigiPOT1.13 (A1), MUX1.6 (S2B), R1.1
VSS: DigiPOT1.2 (B2), DigiPOT1.14 (B1), MUX1.3 (S1B), R2.2
Xctrl: DigiPOT1.4 (W2), MUX1.13 (S4B)
Yctrl: DigiPOT1.12 (W1), MUX1.10 (D3B)

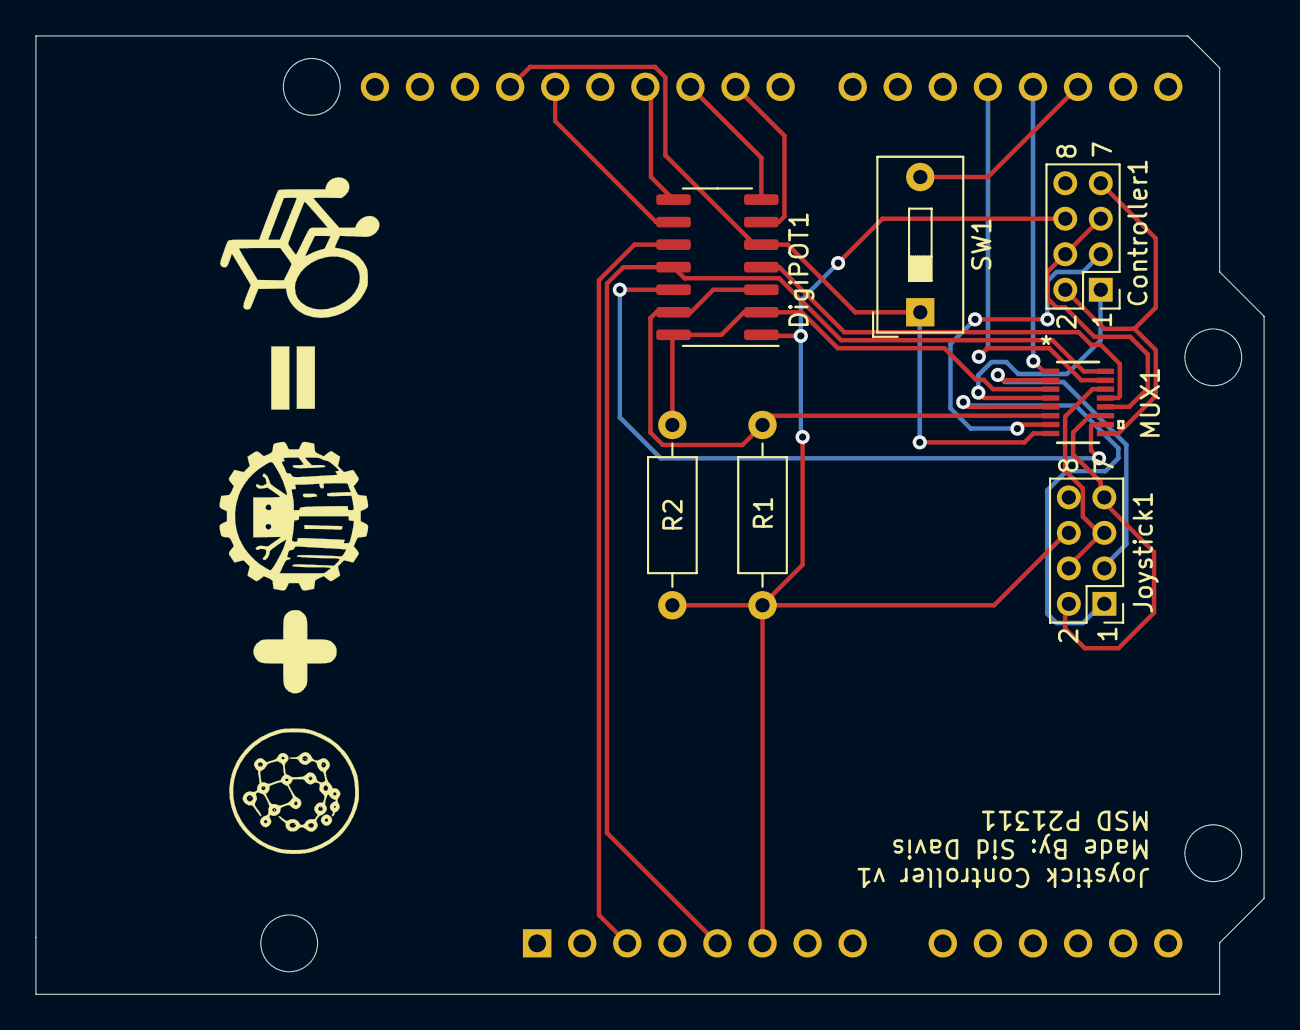
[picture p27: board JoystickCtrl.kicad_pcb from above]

Board: 2 copper layers, 69.2 x 54.0 mm, 8 parts (1 on the bottom side), 23 nets.

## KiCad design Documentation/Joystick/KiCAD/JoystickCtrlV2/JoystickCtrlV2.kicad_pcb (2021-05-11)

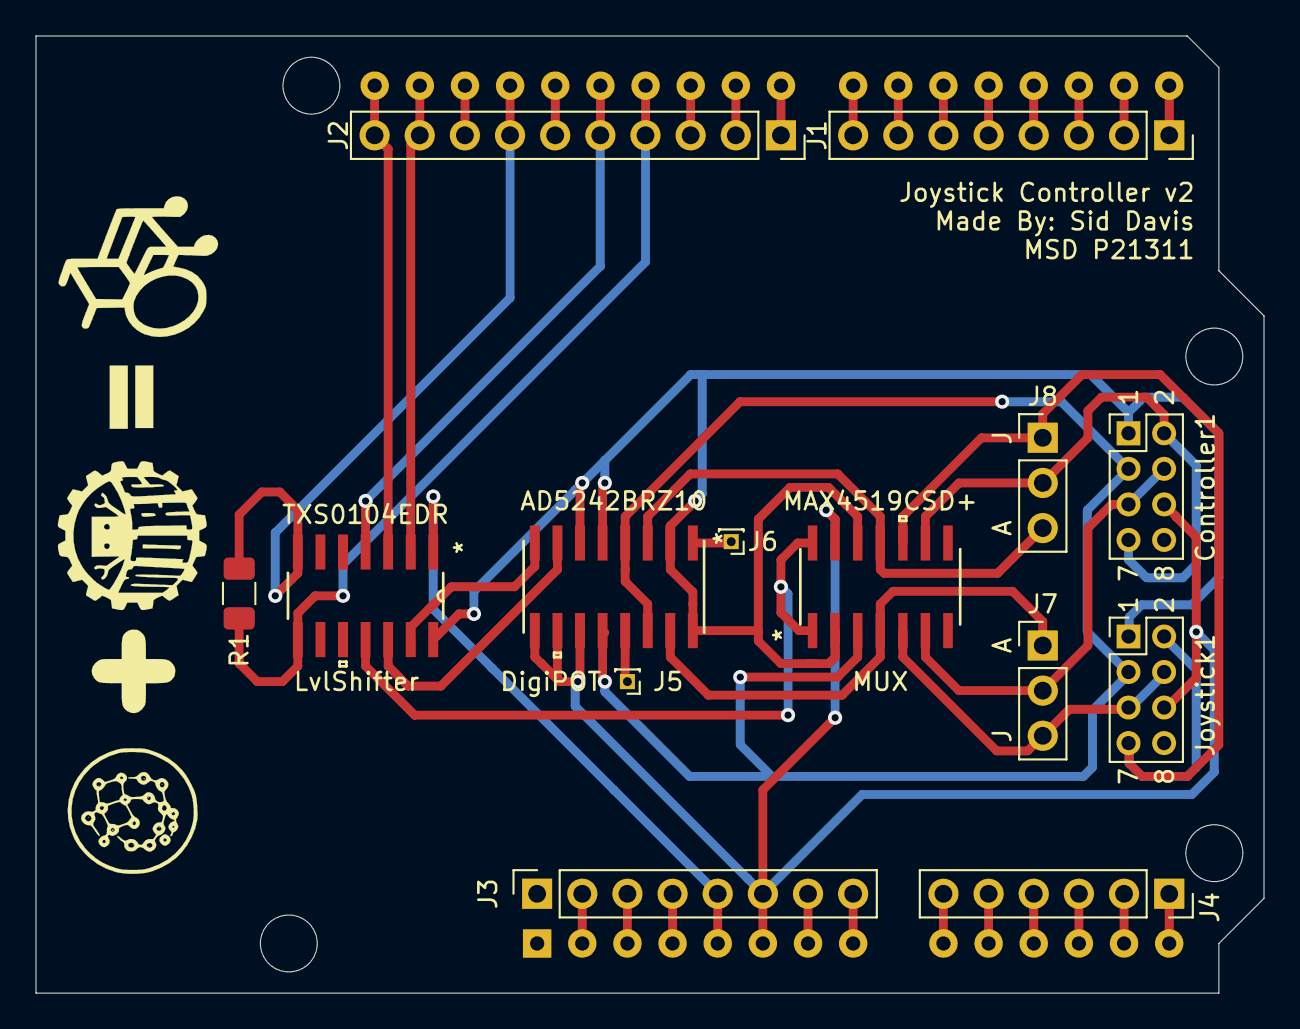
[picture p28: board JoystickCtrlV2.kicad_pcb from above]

Board: 2 copper layers, 69.1 x 53.8 mm, 15 parts (1 on the bottom side), 42 nets.

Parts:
A1: Arduino_UNO_R3; Arduino_UNO_R3_WithMountingHoles
Controller1: Conn_02x04_Odd_Even; PinHeader_2x04_P2.00mm_Vertical
DigiPOT: AD5242BRZ10
J1, J3: Conn_01x08_Male; PinSocket_1x08_P2.54mm_Vertical
J2: Conn_01x10_Male; PinSocket_1x10_P2.54mm_Vertical
J4: Conn_01x06_Male; PinSocket_1x06_P2.54mm_Vertical
J5: O2; PinHeader_1x01_P1.00mm_Vertical
J6: O1; PinHeader_1x01_P1.00mm_Vertical
J7: Y; PinHeader_1x03_P2.54mm_Vertical
J8: X; PinHeader_1x03_P2.54mm_Vertical
Joystick1: Conn_02x04_Odd_Even; PinHeader_2x04_P2.00mm_Vertical
LvlShifter: TXS0104EDR
MUX: MAX4519CSD+; MAX4519CSD&plus_
R1: 10k; R_1206_3216Metric

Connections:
+2V5: Controller1.1, DigiPOT.2, DigiPOT.5, DigiPOT.6, DigiPOT.16, Joystick1.1, LvlShifter.14, MUX.2, MUX.12
+5V: A1.5, J3.5, LvlShifter.1
-2V5: Controller1.3, DigiPOT.4, DigiPOT.12, DigiPOT.14, Joystick1.3, MUX.3
Ard_MUX: A1.27, J2.5, LvlShifter.4
Ard_SCL: A1.32, J2.10, LvlShifter.3
Ard_SDA: A1.31, J2.9, LvlShifter.2
Ctrl_MUX: LvlShifter.11, MUX.1, MUX.14
Ctrl_X: Controller1.2, Controller1.7, J8.2, MUX.9
Ctrl_Y: Controller1.4, Controller1.5, J7.2, MUX.6
Digi_SCL: DigiPOT.7, LvlShifter.12
Digi_SDA: DigiPOT.8, LvlShifter.13
Digi_X: DigiPOT.3, J8.3, MUX.11
Digi_Y: DigiPOT.15, J7.1, MUX.4
GNDREF: A1.6, A1.7, A1.29, Controller1.6, DigiPOT.9, DigiPOT.10, DigiPOT.11, J2.7, J3.6, J3.7, Joystick1.6, LvlShifter.7, MUX.13, R1.2
Joy_X: J8.1, Joystick1.2, Joystick1.7, MUX.10
Joy_Y: J7.3, Joystick1.4, Joystick1.5, MUX.5
unnamed: A1.2, J3.2
unnamed: A1.3, J3.3
unnamed: A1.4, J3.4
unnamed: A1.8, J3.8
unnamed: A1.9, J4.6
unnamed: A1.10, J4.5
unnamed: A1.11, J4.4
unnamed: A1.12, J4.3
unnamed: A1.13, J4.2
unnamed: A1.14, J4.1
unnamed: A1.15, J1.1
unnamed: A1.16, J1.2
unnamed: A1.17, J1.3
unnamed: A1.18, J1.4
unnamed: A1.19, J1.5
unnamed: A1.20, J1.6
unnamed: A1.21, J1.7
unnamed: A1.22, J1.8
unnamed: A1.23, J2.1
unnamed: A1.24, J2.2
unnamed: A1.25, J2.3
unnamed: A1.28, J2.6
unnamed: A1.30, J2.8
unnamed: DigiPOT.1, J6.1
unnamed: DigiPOT.13, J5.1
Shft_En: A1.26, J2.4, LvlShifter.8, R1.1

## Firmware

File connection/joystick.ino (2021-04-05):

// Communicate with DigiPOT over SPI
#define DEBUG 1

#define CLK_PIN  13
#define MISO_PIN 12
#define MOSI_PIN 11
#define SS_PIN   10
#define SHDN_PIN 9

#define EN_MUX_PIN 4
#define S_MUX_PIN 3

const int MECHANICAL = 0;
const int ELECTRICAL = 1;
int mux_state = 0;

const int XPOT = 0;
const int YPOT = 1;
int x_pos = 127;
int y_pos = 127;

void digitalPotWrite(int address, int value);
void SPI_transfer(int value, int bits);

void setup() {
  while(!Serial);
  Serial.begin(9600);

  if (DEBUG) Serial.println("Joystick Controller in DEBUG mode. Feedback Enabled");

  // put your setup code here, to run once:
  pinMode(S_MUX_PIN, OUTPUT);
  pinMode(EN_MUX_PIN, OUTPUT);
  pinMode(CLK_PIN, OUTPUT);
  pinMode(MISO_PIN, INPUT);
  pinMode(MOSI_PIN, OUTPUT);
  pinMode(SS_PIN, OUTPUT);
  pinMode(SHDN_PIN, OUTPUT);

  // Mux
  digitalWrite(EN_MUX_PIN, LOW); // enable mux
  digitalWrite(S_MUX_PIN, mux_state);
  // DigiPOT
  digitalWrite(SHDN_PIN, HIGH);

  digitalPotWrite(XPOT, x_pos);
  digitalPotWrite(YPOT, y_pos);

}

void loop() {
  if (Serial.available()) {
    // parse command
    char cmd = Serial.read();
    switch(cmd) {
      case 'X':
      case 'x':
        setX();
        Serial.print('0');
        break;
      case 'Y':
      case 'y':
        setY();
        Serial.print('0');
        break;
      case 'M':
      case 'm':
        toggleMux();
        Serial.print('1');
        break;
      case '\n':
      case '\r':
      case '\t':
      case ' ':
      case ',':
        break;
      default:
        Serial.print('1');
    }
  }
}

void setX() {
  // get Y value
  int input = Serial.parseInt();
  if (DEBUG) {
    Serial.print("Value received: ");
    Serial.println(input);
  }
  // force within bounds
  input = min(max(input, -100), 100);
  if (DEBUG) {
    Serial.print("After Bounding: ");
    Serial.println(input);
  }
  // map [-100, 100] to [0, 255]
  x_pos = map(input, -100, 100, 0, 255);
  if (DEBUG) {
    Serial.print("Mapped Position: ");
    Serial.println(x_pos);
  }
  // commit the value
  digitalPotWrite(XPOT, x_pos);
  if (DEBUG) {
    Serial.print("The X rail has been set to position ");
    Serial.println(x_pos);
  }
}

void setY() {
  // get Y value
  int input = Serial.parseInt();
  if (DEBUG) {
    Serial.print("Value received: ");
    Serial.println(input);
  }
  // force within bounds
  input = min(max(input, -100), 100);
  if (DEBUG) {
    Serial.print("After Bounding: ");
    Serial.println(input);
  }
  // map [-100, 100] to [0, 255]
  y_pos = map(input, -100, 100, 0, 255);
  if (DEBUG) {
    Serial.print("Mapped Position: ");
    Serial.println(y_pos);
  }
  // commit the value
  digitalPotWrite(YPOT, y_pos);
  if (DEBUG) {
    Serial.print("The Y rail has been set to position ");
    Serial.println(y_pos);
  }
}

void toggleMux() {
  if (mux_state == ELECTRICAL) {
    mux_state = MECHANICAL;
    digitalWrite(S_MUX_PIN, MECHANICAL);
    if (DEBUG) Serial.println("Mux Switch set to MECHANICAL");
  } else {
    mux_state = ELECTRICAL;
    digitalWrite(S_MUX_PIN, ELECTRICAL);
    if (DEBUG) Serial.println("Mux Switch set to ELECTRICAL");
  }
}

void digitalPotWrite(int address, int value) {
  digitalWrite(SS_PIN, LOW);
  delay(1);

  SPI_transfer(address, 2);
  SPI_transfer(value, 8);
  delay(1);

  digitalWrite(SS_PIN, HIGH);
}

void SPI_transfer(int value, int bits) {
  const int FREQ = 20; //kHz
  float T = 1/FREQ * 1000.0;
  int quarter_delay = round(T/4);
  for (int i = bits - 1; i >= 0; i--) {
    bool tx_bit = bitRead(value, i);
    digitalWrite(MOSI_PIN, tx_bit);
    delayMicroseconds(quarter_delay);
    digitalWrite(CLK_PIN, HIGH);
    delayMicroseconds(2 * quarter_delay);
    digitalWrite(CLK_PIN, LOW);
    delayMicroseconds(quarter_delay);
  }
}

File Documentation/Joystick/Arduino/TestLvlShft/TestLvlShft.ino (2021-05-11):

// Code created by Sid Davis for MSD P21311

#define DEBUG 1

// pins
#define SDA A4
#define SCL A5
#define MUX 12
#define LVL_EN 11

// consts
#define ELECTRICAL 0
#define MECHANICAL 1

// state variables
bool sda_state = false;
bool scl_state = false;
bool mux_state = false;
bool lvl_enabled = false;

void setup() {
  // put your setup code here, to run once:
  pinMode(SDA, OUTPUT);
  pinMode(SCL, OUTPUT);
  pinMode(MUX, OUTPUT);
  pinMode(LVL_EN, OUTPUT);

  digitalWrite(SDA, sda_state);
  digitalWrite(SCL, scl_state);
  digitalWrite(MUX, mux_state);
  digitalWrite(LVL_EN, lvl_enabled);

  while(!Serial);
  Serial.begin(9600);
  if (DEBUG) Serial.println("Joystick Controller in DEBUG mode. Feedback Enabled");
}

void loop() {
  // put your main code here, to run repeatedly:
  if (Serial.available()) {
    // parse command
    char cmd = Serial.read();
    switch(cmd) {
      case 'D':
      case 'd':
        toggleSDA();
        break;
      case 'C':
      case 'c':
        toggleSCL();
        break;
      case 'M':
      case 'm':
        toggleMux();
        break;
      case 'O':
      case 'o':
        toggleLvlOut();
        break;
      case '\n':
      case '\r':
      case '\t':
      case ' ':
      case ',':
        break;
    }
  }
}

void toggleSDA() {
  if (sda_state == 0) {
    sda_state = 1;
    digitalWrite(SDA, sda_state);
    if (DEBUG) Serial.println("SDA set to 1");
  } else {
    sda_state = 0;
    digitalWrite(SDA, sda_state);
    if (DEBUG) Serial.println("SDA set to 0");
  }
}

void toggleSCL() {
  if (scl_state == 0) {
    scl_state = 1;
    digitalWrite(SCL, scl_state);
    if (DEBUG) Serial.println("SCL set to 1");
  } else {
    scl_state = 0;
    digitalWrite(SCL, scl_state);
    if (DEBUG) Serial.println("SCL set to 0");
  }
}

void toggleMux() {
  if (mux_state == ELECTRICAL) {
    mux_state = MECHANICAL;
    digitalWrite(MUX, mux_state);
    if (DEBUG) Serial.println("Mux set to MECHANICAL");
  } else {
    mux_state = ELECTRICAL;
    digitalWrite(MUX, mux_state);
    if (DEBUG) Serial.println("Mux set to ELECTRICAL");
  }
}

void toggleLvlOut() {
  if (lvl_enabled == 1) {
    lvl_enabled = 0;
    digitalWrite(LVL_EN, lvl_enabled);
    if (DEBUG) Serial.println("Lvl Shft set OFF");
  } else {
    lvl_enabled = 1;
    digitalWrite(LVL_EN, lvl_enabled);
    if (DEBUG) Serial.println("Lvl Shft set ON");
  }
}

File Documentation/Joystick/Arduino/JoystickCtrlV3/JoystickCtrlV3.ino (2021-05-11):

// control joystick using servos & potentiometers

#define DEBUG 0

// Libraries
#include <Servo.h>

// pins
#define SERVO_X 3
#define SERVO_Y 5

// consts
#define ELECTRICAL 0
#define MECHANICAL 1
#define RAMP_DELAY 10
#define MIN_SET 0
#define MAX_SET 180

// state variables
bool ctrl_state = MECHANICAL;
byte x_goal = 90;
byte y_goal = 90;
byte x_pos = 90;
byte y_pos = 90;

// servo objects
Servo servo_x;  
Servo servo_y;  

void setup() {
  // put your setup code here, to run once:

  // initialize the servos
  servo_x.attach(SERVO_X);
  servo_y.attach(SERVO_Y);
  servo_x.write(x_pos);
  servo_y.write(y_pos);
  
  // Wait for the Serial Connection
  while(!Serial);
  Serial.begin(9600);
  if (DEBUG) Serial.println("Joystick Controller in DEBUG mode. Feedback Enabled");

}

void loop() {
  // put your main code here, to run repeatedly:
  if (Serial.available()) {
    // parse command
    char cmd = Serial.read();
    switch(cmd) {
      case 'X':
      case 'x':
        Serial.print(setX());
        break;
      case 'Y':
      case 'y':
        Serial.print(setY());
        break;
      case 'M':
      case 'm':
//        Serial.print(toggleMux());
        Serial.print(1);
        break;
      case 'O':
      case 'o':
        //Serial.print(toggleLvlOut());
        Serial.print(1);
        break;
      case '\n':
      case '\r':
      case '\t':
      case ' ':
      case ',':
        break;
      default:
        Serial.print(1);
    }
  }

  if (x_goal > x_pos) {
    x_pos++;
    servo_x.write(x_pos);
    delay(RAMP_DELAY);
  } else if (x_goal < x_pos) {
    x_pos--;
    servo_x.write(x_pos);
    delay(RAMP_DELAY);
  }

  if (y_goal > y_pos) {
    y_pos++;
    servo_y.write(y_pos);
    delay(RAMP_DELAY);
  } else if (y_goal < y_pos) {
    y_pos--;
    servo_y.write(y_pos);
    delay(RAMP_DELAY);
  }
}

int setX() {
  int error = 0;
  // grab the value to set
  int input = Serial.parseInt();

  // check for bounding
  if ((input > 100) || (input < -100)) {
    if (DEBUG) Serial.println("Received value for 'SET X' is out of range, but has been clipped");
    error = 1;
  }
  input = min(max(input, -100), 100);

  // map to a byte and commit
  x_goal = byte(map(input, -100, 100, MIN_SET, MAX_SET));
  if (DEBUG) {
    Serial.print("X has been set to ");
    Serial.println(x_goal);
  }
  return error;
}

int setY() {
  int error = 0;
  // grab the value to set
  int input = Serial.parseInt();

  // check for bounding
  if ((input > 100) || (input < -100)) {
    if (DEBUG) Serial.println("Received value for 'SET Y' is out of range, but has been clipped");
    error = 1;
  }
  input = min(max(input, -100), 100);

  // map to a byte and commit
  y_goal = byte(map(input, -100, 100, MIN_SET, MAX_SET));
  if (DEBUG) {
    Serial.print("Y has been set to ");
    Serial.println(y_goal);
  }
  return error;
}

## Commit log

2021-03-08 added turn left/right print in side to side detection section
2021-03-08 Added dual cameras to left_right as main function
2021-03-15 Reset device pose, added new path planning
2021-03-22 few more print/readme adjustments
2021-04-12 Updated arduino to close nicely
2021-04-28 Update README.md
    added turning into high level code flow in readme
2021-05-11 3D Models from OnShape
    [CameraAssembly.step, Footrest2CameraMount.step, Footrest2CameraMount.stl, JoystickCtrlV3.step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]
2021-05-11 Joystick Docs, Code, & PCBs
    [200-MSP-1-T3-B1-M2-PE-rev2.step, Bom_8537414.xlsx, JoystickCtrl-B_Cu.gbr, JoystickCtrl-B_Mask.gbr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]
2021-05-11 Camera Docs
2021-05-11 MSD Documentation
    HoQ, PRP, BOM, & Risks
    [House of Quality.xlsx, Purchasing List.xlsx, Risk Management.xlsx]

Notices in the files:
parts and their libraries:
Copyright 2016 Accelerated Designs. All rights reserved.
